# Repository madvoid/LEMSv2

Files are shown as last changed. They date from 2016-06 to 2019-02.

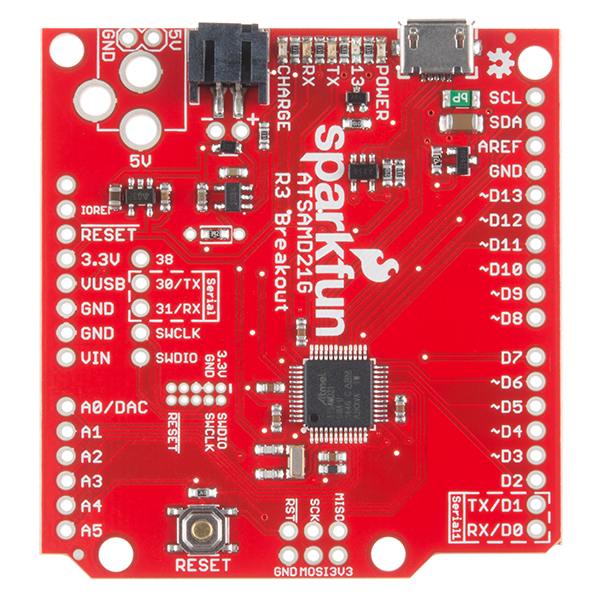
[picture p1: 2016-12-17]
Hardware Information/PCB/SAMD21 Breakout Board.jpg

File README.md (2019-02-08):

# LEMSv2
This is the repository for the second version of the LEMS Sensor Stations. Stay tuned, information will be added as it is generated. A majority of the documentation will be added to this file. Long-term future development will happen at https://github.com/UtahEFD/LEMSv2.

### General TODO

1. Check validity of filenames with more than 8 characters
2. Decagon, the manufacturer of the 5TM soil sensors, has changed their name to Meter, and the 5TM is now called the ECH20 5TM. The DS2 is now called the Atmos 22. The documentation will need to be changed and will probably be done slowly.
3. Major Change: Change the code to read parameters from a text file on the SD card. See if possible to read code from SD card.
4. Delete or separate "File List" from README? Makes it clunky, hard to keep updated. Goal is for files to self explanatory 
5. Update DS2 code to use EnviroDIY's SDI12 library instead of custom library

### PCB TODO
1. Change the parts in the eagle files for BOM lines 11, 29, 30. These parts were out of stock and were replaced by different parts during manufacturing.

### File List
* Code/
  * `Code Instructions.md` - Instructions for uploading
  * LEMSv2/
    * `LEMSv2.ino` - LEMS Arduino Code
    * `DS3231_Alarm1.h` - Header file for corresponding `.cpp` file
    * `DS3231_Alarm1.cpp` - File used to set DS3231 Alarm 1. Developed in test code then copied to this folder
    * `d5TM.h` - Header file for corresponding `.cpp` file
    * `d5TM.cpp` - Library used to interact with 5TM. Developed in test code then copied to this folder
  * Test Code/
    * ADS1115_Test/
      * `ADS1115_Test.ino` - Test code for ADS1115 ADC
    * DS3231_Test/
      * `DS3231_Test.ino` - Test code for DS3231 RTC. Test DS3231 alarm 1
      * `DS3231_Alarm1.h` - Header file for corresponding `.cpp` file
      * `DS3231_Alarm1.c` - Library used to set DS3231 Alarm 1. Developed in here then copied to main code folder
    * DS2_Test/
      * `DS2_Test.ino` - Test code for DS2 anemometer
      * `DS2.h` - Header file for corresponding `.cpp` file
      * `DS2.cpp` - Library used to interact with DS2. Developed here then copied to main code folder
      * `LICENSE` - License to be included with the `SDI12_Zero` library
      * `LICENSE-examples.md` - License to be included with the `SDI12_Zero` library
      * `SDI12_Zero.h` - Header file for corresponding `.cpp` file
      * `SDI12_Zero.cpp` - Library used by DS2 library to interact with DS2. Implements the SDI12 protocal for Arduino Zero.
    * Li200_Test/
      * `Li200_Test.ino` - Test Li200 with intermediate values in calculations printed
    * Teros21_Test/
      * `Teros21_Test.ino` - Test Teros21 and library.
    * Test_5TM/
      * `Test_5TM.ino` - Test code for 5TM Library. 5TM has been working since LEMSv1 but is now made into a library.
      * `d5TM.h` - Header file for corresponding `.cpp` file
      * `d5TM.cpp` - Library used to interact with 5TM. Developed here then copied to main code folder
  * Time_Set/
    * `Time_Set.ino` - Code used to set the time on the DS3231 real time clock
* Data Manipulation/
  * `LemsPlot.m` - View LEMSv2 data plots. Not perfectly adaptable to any file, but will work for a fully instrumented station. To work properly, requires the [Intelligent Dynamic Date Ticks](https://www.mathworks.com/matlabcentral/fileexchange/27075-intelligent-dynamic-date-ticks) file from MathWorks. Can work without it though by commenting out the lines that use it.
  * `importfile.m` - Used to import the LEMSv2 data files. Can only be used on data files from fully instrumented LEMS.
* Hardware Information/
  * `Bill of Materials.xlsx` - Complete parts list
  * `Calibration Constants.xlsx` - Calibration constants for various instruments. For now, only contains Li200 constants.
  * Data Sheets/
    * Multiple data sheets for components
  * Li200R Base/
    * Solidworks/
      * Contains Solidworks files for Li200R base
    * STL Files/
      * Contains print ready STL files for Li200R base
    * `Build Instructions.md` - Tools required for making the Li200R base
  * MLX Housing/
    * `MLX Housing Build Instructions` - Build instructions for MLX90615 housing
  * PCB/
    * `LEMSv2 Board.pdf` - PDF of PCB for easy reference
    * `LEMSv2 Schematic.pdf` - PDF of schematic for easy reference
    * `SAMD21 Breakout Board.jpg` - Reference picture for microcontroller board
  * `Pin List.xlsx` - Pin connection list for SAMD21 Dev Breakout Board
  * `Possible Parts.txt` - Potential parts/Manufacturers to add/use in the future
  * Transimpedance Amplifier/
    * `Transimpedance_Amplifier_Calculations.ipynb` - Jupyter notebook containing transimpedance amplifier calculations
  * `Wiring Information.xlsx` - Information about wiring. What connects to what, etc. Work in progress.
* `LICENSE.TXT` - License
* PCB/
  * LEMSv2 PCB/
    * `Centroid_ScreamingCircuits_smd.ulp` - Eagle ULP script to create centroid data for screaming circuits
    * Gerbers/
      * Contains gerbers for board, plus the panelized gerbers supplied by OSH Park. Also contains the centroid file for Screaming Circuits.
    * `LEMSv2.sch` - LEMSv2 shield schematic
    * `LEMSv2.brd` - LEMSv2 shield layout
    * `OSH_DesignRules.dru` - Eagle design rules for OSH Park
    * `OSHPark_2layer_Eagle7.2.cam` - Modified cam job for OSH Park
  * LEMSv2 PCB Library/
    * `LEMSv2.lbr` - Parts used in the LEMSv2 shield
* `Possible Problems.md` - List of potential hardware problems in the LEMS. Prefer to not have duplicate entries, i.e. one line per problem.
* `README.md` - If you read this line you're actually reading the README. Good job!

### Dependencies
Only 3rd party software dependencies are included in this list. Libraries built into the Arduino software or created for the LEMSv2 software isn't included. You will need the most recent version of the [Arduino IDE](https://www.arduino.cc/en/Main/Software) installed.

* [Adafruit RTC Library](https://github.com/adafruit/RTClib)
* [Adafruit SHT31 Library](https://github.com/adafruit/Adafruit_SHT31)
* [Adafruit Sensor Library](https://github.com/adafruit/Adafruit_Sensor)
* [Adafruit BMP280 Library](https://github.com/adafruit/Adafruit_BMP280_Library)
* [Adafruit MLX90614 Library](https://github.com/adafruit/Adafruit-MLX90614-Library)
* [EnviroDIY SDI-12 Library](https://github.com/EnviroDIY/Arduino-SDI-12) 
* [Soligen2010's fork of the Adafruit ADS1x15 Library](https://github.com/soligen2010/Adafruit_ADS1X15). The default Adafruit ADS1x15 library **doesn't** work.
* In addition, the Sparkfun SAMD21 [board definition](https://raw.githubusercontent.com/sparkfun/Arduino_Boards/master/IDE_Board_Manager/package_sparkfun_index.json
  ) needs to be installed into the Arduino IDE. See [here](https://learn.sparkfun.com/tutorials/samd21-minidev-breakout-hookup-guide/setting-up-arduino) for more info.

### Miscellaneous Notes

- ADS1115 single ended resolution calculation information can be found [here](https://e2e.ti.com/support/data_converters/precision_data_converters/f/73/t/489070)
- ADS1115 over range input information can be found [here](https://e2e.ti.com/support/data_converters/precision_data_converters/f/73/p/398187/1407689#1407689) and [here](https://e2e.ti.com/support/data_converters/precision_data_converters/f/73/t/378122)

### Acknowledgements

* Thanks to [Sparkfun](https://www.sparkfun.com) and [Adafruit](https://www.adafruit.com) for Arduino libraries, components, tutorials, and eagle parts. Many designs and eagle components are directly used from them. Also thanks to [OSH Park](www.oshpark.com) and [Screaming Circuits](www.screamingcircuits.com) for the excellent PCBs and assembly. They were instrumental in getting LEMSv2 completed.

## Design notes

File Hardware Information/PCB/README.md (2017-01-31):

# README.md

These files are here for quick reference. For gerber files please see the ../../PCB folder.

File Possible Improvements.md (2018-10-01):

# Possible Improvements

This document outlines possible improvements or repeatable bugs that need to be fixed.

* Multiple LEMS have now failed in an unusual way. The LEMS fails, the SD card has weird, corrupted files on it, and the LEMS may or may not blink on a restart. It is either correlated with high moisture or high electromagnetic interference (lightning). It often damages that MLX90614 beyond repair, but may damage other things. The LEMS behaves erratically after this happens.
* The DS3231 chip may reset back to 1/1/2000 00:00:00 on a restart. This is probably because of a power cycle issue, and is currently being investigated.
* Add wireless transmission for remote monitoring
* The microcontroller that runs the whole thing is currently separate from the other circuitry. It would be nice to incorporate the two so we aren’t dependent on a separate manufacturer for the boards
* The real-time clock is one of the most unreliable components on the board. Improving the reliability of this through hardware or software would improve data quality.
* Adding a GPS chip for location and accurate time would be beneficial for multiple reasons. This would help keep the real-time clock calibrated
* Making the board larger and have screw terminals for every pin would increase the flexibility of the board
* Adding electronic reliability components (fuses, transient voltage suppressors, etc.) would help with overall reliability.
* Adding a thermocouple chip would increase measurement flexibility.
* The hardware around the electronics can always use improvements!

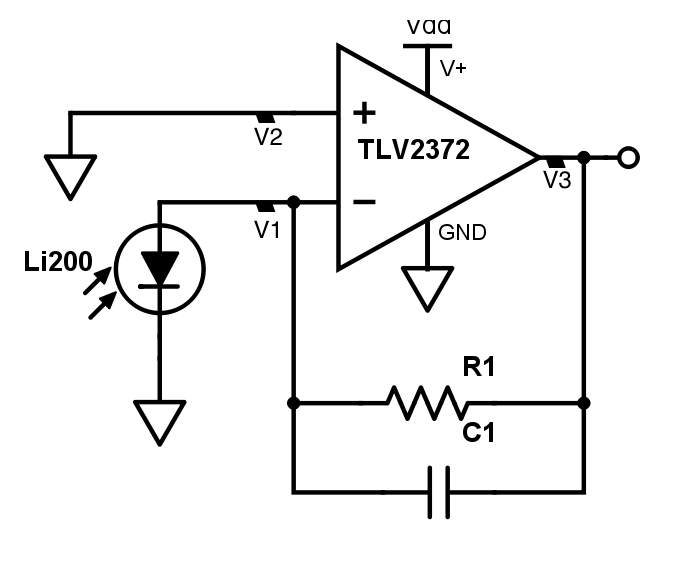
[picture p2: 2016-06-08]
Hardware Information/Transimpedance Amplifier/Li200-Transimpedance-Amplifier.png

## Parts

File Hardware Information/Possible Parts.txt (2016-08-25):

*** Possible parts to use for LEMSv2 ***
Moved from "Bill of Materials.xlsx"

Custom Enclosure:
- http://www.toollessplasticenclosures.com

Good Headers: 
- http://www.digikey.com/product-search/en/connectors-interconnects/rectangular-connectors-headers-receptacles-female-sockets/1442548?k=&pkeyword=&pv88=24&pv88=7&pv88=26&pv88=10&FV=fffc0023%2C1640001%2C1680001%2Cfff40016%2Cfff802f4&mnonly=0&newproducts=0&ColumnSort=88&page=1&stock=1&quantity=0&ptm=0&fid=0&pageSize=25

Radiation Shield: 
- http://www.ambientweather.com/amwesrpatean.html#caption
- 3D print one

Fan:
http://www.mouser.com/ProductDetail/Orion-Fans/OD4010-05MB/?qs=sGAEpiMZZMt9MS9kROxCw6QJH9LIBAB%2fCEdiIeq2Xcc%3d
http://catalog.pelonistechnologies.com/item/automotive-fans-and-blowers/all-categories-micro-fans-rfa1504u-micro-fan/rfa1504u
http://www.digikey.com/en/supplier-centers/d/delta-product-groups-fans
http://www.digikey.com/product-search/en/fans-thermal-management/dc-fans/1179730?FV=38007c%2C3800fb%2C3801a9%2Cfff40012%2Cfff80052&mnonly=0&newproducts=0&ColumnSort=2&page=3&stock=1&pbfree=0&rohs=0&quantity=&ptm=0&fid=0&pageSize=25

Jumper Cables:
- http://www.digikey.com/product-search/en/cable-assemblies/flat-flex-ribbon-jumper-cables/1573391?k=&pkeyword=&pv316=2&FV=134004e%2C13400ac%2C134019b%2C13407ff%2C134098f%2C13409fe%2C1340fa6%2Cfff40018%2Cfff8020f%2C40800cf&mnonly=0&newproducts=0&ColumnSort=0&page=1&stock=1&quantity=0&ptm=0&fid=0&pageSize=25
- http://www.digikey.com/product-search/en/cable-assemblies/flat-flex-cables-ffc-fpc/1573426?k=&pkeyword=&pv31=241&pv31=239&FV=7c00ef%2C7c00f1%2C7c00f3%2C134000c%2C1340700%2C1340736%2C1640001%2Cfff40018%2Cfff80232%2C1600006&mnonly=0&newproducts=0&ColumnSort=0&page=1&stock=1&quantity=0&ptm=0&fid=0&pageSize=25

Resettable fuse:
http://www.digikey.com/product-search/en/circuit-protection/ptc-resettable-fuses/656272?k=&pkeyword=&pv683=127&FV=400006%2C403989%2Caac0065%2Caac0073%2Caac0074%2Caac007d%2Caac007f%2Caac0090%2Caac0092%2Caac0093%2Caac0094%2Caac0095%2Caac009c%2Caac00a0%2Caac00a5%2Caac00aa%2Caac00ae%2Cfff4000a%2Cfff80390%2Caa80061&mnonly=0&newproducts=0&ColumnSort=0&page=1&stock=1&quantity=0&ptm=0&fid=0&pageSize=25

PCB Assembly:
http://pcbshopper.com
http://www.7pcb.com
https://www.screamingcircuits.com
http://www.4pcb.com/Assembly-Services.html
https://macrofab.com
https://circuithub.com

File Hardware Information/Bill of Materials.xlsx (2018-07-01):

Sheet: Full Device
 |  |  | Shipping costs and taxes not included! |  | Red cells indicate values calculated from quotes |  |  |  | Quantity: | 12
Information |  |  | Ideal Cost/Unit |  | Ideal Cost/10 Units |  | Ideal Cost/25 Units |  | Actual (Paid) Cost |  | Ordering |  |  |  | Notes
Number | Part | Quantity/Prototype | Cost/Unit | Total Quantity Cost | Cost/Unit | Prototype Cost | Cost/Unit | Prototype Cost | Cost/Unit | Prototype Cost | Source | Distributor Part Number | Package | Link
 | CR1220 Battery | 1 | $0.90 | $0.90 | $0.81 | $8.12 | $0.81 | $20.30 | $0.81 | $9.74 | Digikey | P033-ND | N/A | http://www.digikey.com/product-detail/en/panasonic-bsg/CR1220/P033-ND/269740 | Possible different source? Check footprint carefully if so
 | Noco 2.5 Watt Solar Panel | 1 | $24.95 | $24.95 | $24.95 | $249.50 | $24.95 | $623.75 | $24.95 | $299.40 | Amazon | N/A | N/A | https://www.amazon.com/NOCO-Battery-BLSOLAR2-Charger-Maintainer/dp/B00B7GC50Y | Other options available, see https://no.co/products/solar. Noco UPC: 0-46221-12069-1. More expensive on Noco website. Also known as BLSOLAR2
 | Noco 12V 2A Regulator | 1 | $12.95 | $12.95 | $12.95 | $129.50 | $12.95 | $323.75 | $12.95 | $155.40 | Amazon | N/A | N/A | https://www.amazon.com/NOCO-GC027-12V-Flex-Regulator/dp/B00H36Y65O | Other options available, see https://no.co/products/solar. Noco UPC: 0-46221-13106-2. More expensive on Noco website. Also known as GC027
 | SAMD21 Dev Board | 1 | $24.95 | $24.95 | $23.70 | $237.00 | $22.46 | $561.50 | $23.70 | $284.40 | Sparkfun | DEV-13672 | N/A | https://www.sparkfun.com/products/13672
 | Arduino Stacking Headers | 1 | $1.95 | $1.95 | $1.75 | $17.55 | $1.75 | $43.88 | $1.75 | $21.06 | Digikey | 1528-1074-ND | N/A | http://www.digikey.com/product-search/en?mpart=85&vendor=1528 | Alt. Source: https://www.adafruit.com/product/85
 | Printed Circuit Board (PCB) | 1 | $16.34 | $16.34 | $16.34 | $163.37 | $16.34 | $408.42 | $27.62 | $331.50 | Osh Park | N/A | N/A | http://www.oshpark.com | 3.38"x2.90" standard. 7.46"x6.51" panelized. 4x/panel. Osh Park prices $5/in^2 for 3. Actual cost has super swift service added. Medium run not considered
 | PCB Assembly | 1 | $70.73 | $70.73 | $70.73 | $707.33 | $70.73 | $1768.31 | $70.73 | $848.79 | Screaming Circuits | N/A | N/A | http://www.screamingcircuits.com | Ideal costs are hard to calculate without quote. Student discount included
 | PCB Turnkey Parts | 1 | $58.59 | $58.59 | $58.59 | $585.94 | $58.59 | $1464.85 | $58.59 | $703.13 | Screaming Circuits | N/A | N/A | http://www.screamingcircuits.com | Ideal costs are hard to calculate without quote. See Shield Parts sheet for part breakdown without "Turnkey Tax"
 | 12V 5.5Ah Sealed Lead Acid Battery | 1 | $8.39 | $8.39 | $8.39 | $83.90 | $8.39 | $209.75 | $32.00 | $384.00 | BatterySharks | N/A | N/A | https://www.batterysharks.com/12-Volt-5-5-Amp-Sealed-Lead-Acid-Battery-p/12v-5.5ah_ups12-5.5.htm | BatterySharks is US source. The $30 ones were bought in europe, explaining the price. F2 terminals are typically used
 | Seahorse SE-120 Waterproof Case | 1 | $11.83 | $11.83 | $11.83 | $118.30 | $11.83 | $295.75 | $11.83 | $141.96 | Fuerte Cases | SE-120 | N/A | http://www.seahorsecases.com/Seahorse-SE120-Small-Waterproof-Protective-Equipment-Storage-Shipping-Case.html | Available from other sources
 | Radiation Shield | 1 | $39.99 | $39.99 | $39.99 | $399.90 | $39.99 | $999.75 | $39.99 | $479.88 | Ambient Weather | SRS100LX | N/A | http://www.ambientweather.com/amwesrpatean.html | Sometimes available from other sources
 | SHT31 Temp/RH Sensor | 1 | $13.95 | $13.95 | $12.56 | $125.60 | $12.56 | $314.00 | $12.56 | $150.72 | Adafruit | 2857 | N/A | https://www.adafruit.com/products/2857
 | MLX90614 IR Sensor | 1 | $14.95 | $14.95 | $13.46 | $134.60 | $13.46 | $336.50 | $13.46 | $161.52 | Acrobotic | MLX90614 | N/A | https://acrobotic.com/brk-00018 | Can maybe be found on eBay
 | Decagon 5TM Soil Sensor | 2 | $186.00 | $372.00 | $167.00 | $3340.00 | $167.00 | $8350.00 | $334.00 | $4008.00 | Decagon | 5TM | N/A | https://www.decagon.com/en/ | Need quote to order
 | Davis Anemometer | 1 | $106.99 | $106.99 | $106.99 | $1069.90 | $106.99 | $2674.75 | $106.99 | $1283.88 | Hodges Marine | DAV6410 | N/A | http://www.hodgesmarine.com/Davis-Anemometer-F-Vantage-Pro2-153-Vantage-p/dav6410.htm
 | LiCor Li200 Pyranometer | 1 | $270.00 | $270.00 | $259.20 | $2592.00 | $259.20 | $6480.00 | $259.20 | $3110.40 | LiCor | Li-200R | N/A | https://www.licor.com | Can order online or with quote. Unsure whether online gets you quantity discount
 | Wide Range 1/8" Blind Rivet | 3 | $0.08 | $0.25 | $0.08 | $2.46 | $0.08 | $6.14 | $0.25 | $2.95 | McMaster | 97530A030 | N/A | https://www.mcmaster.com/#97530a030/=14t3x41 | Comes in box of 100
 | 1/8" Thick Aluminum Strip | 1 | $0.32 | $0.32 | $0.32 | $3.17 | $0.32 | $7.93 | $0.32 | $3.80 | McMaster | 2474T11 | 6' Long, 1" Wide | https://www.mcmaster.com/#2474t11/=14txki1 | Can get in orders of different lengths
 | Dessicant | 1 | $1.10 | $1.10 | $1.10 | $10.96 | $1.10 | $27.40 | $1.10 | $13.15 | McMaster | 3492T15 | N/A | https://www.mcmaster.com/#3492t15/=14r8wyx | Comes in box of 10
 | Silicone Sealing Washer | 2 | $0.15 | $0.29 | $0.15 | $2.94 | $0.15 | $7.36 | $0.29 | $3.53 | McMaster | 99604A103 | N/A | https://www.mcmaster.com/#99604a103/=14t3xma | Comes in box of 50
 | LiCor Leveling Base | 1 | $22.84 | $22.84 | $22.84 | $228.39 | $22.84 | $570.97 | $22.84 | $274.06 | - | - | - | - | See LiCor_Leveling_Base sheet for details
 | 1/4" Washer | 2 | $0.03 | $0.07 | $0.03 | $0.66 | $0.03 | $1.65 | $0.03 | $0.40 | McMaster | 90107A029 | N/A | https://www.mcmaster.com/#90107a029/=1dc0vgi | Goes around silicon washer to add thickness for rivet to clamp onto. Comes in packs of 100
 | 1&5/16" to 2&1/4" Hose Clamp | 2 | $0.70 | $1.40 | $0.70 | $13.98 | $0.70 | $34.95 | $0.70 | $8.39 | McMaster | 5415K18 | N/A | https://www.mcmaster.com/#5415k18/=178w5hq | Comes in packs of 10
 | SD Card | 1 | $4.55 | $4.55 | $4.55 | $45.50 | $4.55 | $113.75 | $4.55 | $54.60 | Newegg | 9SIA12K0X38348 | N/A | http://www.newegg.com/Product/Product.aspx?item=N82E16820134717 | Can be substituted with other parts
 | MLX90614 Housing | 1 | $6.68 | $6.68 | $6.68 | $66.84 | $6.68 | $167.11 | $6.68 | $80.21 | - | - | - | - | See MLX90614_Housing sheet for details
 |  |  |  | $0.00 |  | $0.00 |  | $0.00 |  | $0.00
 |  |  |  | $0.00 |  | $0.00 |  | $0.00 |  | $0.00
 |  |  | Total Prototype Cost: | $1086.95 | Total Prototype Cost: | $10337.41 | Total Prototype Cost: | $25812.52 | Total Prototype Cost: | $12814.88
 |  |  | Prototype Cost/Unit: | $1086.95 | Prototype Cost/Unit: | $1033.74 | Prototype Cost/Unit: | $1032.50 | Prototype Cost/Unit: | $1067.91

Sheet: Shield Parts
TH = Through Hole |  | SMT = Surface Mount | Shipping costs not included! | Octopart has alt. distributors
Information |  |  |  |  |  | Price/Unit |  | Price/10 Units |  | Price/25 Units |  | Ordering |  |  |  | Notes
Place | Reference Designator | Manufacturer | Manufacturer Part Number | Part Description | Quantity/Board | Cost/Part | Total Quantity Cost | Cost/Part | Total Quantity Cost | Cost/Part | Total Quantity Cost | Source | Distributor Part Number | Package | Distributor Link
Yes | J7, J15-J26 | On Shore Technology Inc. | OSTTE020104 | 2-Pin 3.5mm Screw Terminal | 13 | $0.3800 | $4.94 | $0.3640 | $47.32 | $0.3120 | $101.40 | Digikey | ED2740-ND | 3.5mm Spacing TH | http://www.digikey.com/product-detail/en/on-shore-technology-inc/OSTTE020104/ED2740-ND/2351816
Yes | J27-J30 | On Shore Technology Inc. | OSTTE040104 | 3-Pin 3.5mm Screw Terminal | 4 | $0.6700 | $2.68 | $0.6240 | $24.96 | $0.5616 | $56.16 | Digikey | ED2742-ND | 3.5mm Spacing TH | http://www.digikey.com/product-detail/en/on-shore-technology-inc/OSTTE040104/ED2742-ND/2351818
Yes | PS1 | Traco Power | TSR 1-2450 | DC/DC 5V Regulator | 1 | $6.2000 | $6.20 | $5.7000 | $57.00 | $5.4300 | $135.75 | Mouser | 495-TSR-1-2450 | SIP-3 | http://www.mouser.com/ProductDetail/TRACO-Power/TSR-1-2450/?qs=ckJk83FOD0XFKqda0Mzkgw%3D%3D
No | C1 | Panasonic Electronics | ECA-1HM220 | 22uF 50V Capacitor | 1 | $0.2200 | $0.22 | $0.1530 | $1.53 | $0.1124 | $2.81 | Digikey | P5179-ND | 5mm Diam. Radial TH | http://www.digikey.com/product-detail/en/ECA-1HM220/P5179-ND/245038?curr=usd&WT.z_cid=ref_octopart_dkc_buynow&site=us
Yes | U1 | TE Connectivity | 2041021-3 | SD Card Holder | 1 | $1.7400 | $1.74 | $1.7400 | $17.40 | $1.4900 | $37.25 | Newark | 35R2925 | N/A | http://www.newark.com/te-connectivity/2041021-3/memory-card-connector-sd-9-position/dp/35R2925?CMP=AFC-QO1721829242?gross_price=
Yes | U2 | Maxim Integrated | DS3231SN#T&R | DS3231 Real Time Clock | 1 | $9.9700 | $9.97 | $9.4100 | $94.10 | $7.5276 | $188.19 | Digikey | DS3231SN#T&RCT-ND | SOIC-16 | http://www.digikey.com/product-detail/en/DS3231SN%2523T%26R/DS3231SN%2523T%26RCT-ND/3894827?curr=usd&WT.z_cid=ref_octopart_dkc_buynow&site=us
Yes | R1-R5, R7, R9, R11, R13, R19-R21 | Yageo | RC0805FR-0710KL | 10k 1% 1/8W Resistor | 12 | $0.1000 | $1.20 | $0.0210 | $2.52 | $0.0152 | $4.56 | Digikey | 311-10.0KCRCT-ND | 0805 (Imperial) | http://www.digikey.com/product-detail/en/RC0805FR-0710KL/311-10.0KCRCT-ND/730482?curr=usd&WT.z_cid=ref_octopart_dkc_buynow&site=us
Yes | C2, C4, C7 | Taiyo Yuden | UMK212B7105KG-T | 1uF 50V Ceramic Capacitor | 3 | $0.2100 | $0.63 | $0.1410 | $4.23 | $0.1410 | $10.57 | Digikey | 587-2910-1-ND | 0805 (Imperial) | https://www.digikey.com/product-detail/en/taiyo-yuden/UMK212B7105KG-T/587-2910-1-ND/2649030
Yes | BT1 | Keystone Electronics | 3000 | 12mm Battery Holder | 1 | $0.5800 | $0.58 | $0.5450 | $5.45 | $0.5450 | $13.63 | Digikey | 36-3000-ND | SMT | http://www.digikey.com/product-detail/en/3000/36-3000-ND/227440?curr=usd&WT.z_cid=ref_octopart_dkc_buynow&site=us
Yes | LED1 | Lite-On Inc. | LTST-C190GKT | Green LED | 1 | $0.2700 | $0.27 | $0.1960 | $1.96 | $0.1448 | $3.62 | Digikey | 160-1183-1-ND | 0603 (Imperial) | http://www.digikey.com/product-detail/en/LTST-C190GKT/160-1183-1-ND/269255?curr=usd&WT.z_cid=ref_octopart_dkc_buynow&site=us
Yes | LED2 | Lite-On Inc. | LTST-C190KRKT | Red LED | 1 | $0.2700 | $0.27 | $0.1960 | $1.96 | $0.1448 | $3.62 | Digikey | 160-1436-1-ND | 0603 (Imperial) | http://www.digikey.com/product-detail/en/LTST-C190KRKT/160-1436-1-ND/386816?curr=usd&WT.z_cid=ref_octopart_dkc_buynow&site=us
Yes | R6, R8, R10, R17, R18 | Yageo | RC0805FR-074K3L | 4.3k 1% 1/8W Resistor | 5 | $0.1000 | $0.50 | $0.0210 | $1.05 | $0.0152 | $1.90 | Digikey | 311-4.30KCRCT-ND | 0805 (Imperial) | http://www.digikey.com/product-detail/en/RC0805FR-074K3L/311-4.30KCRCT-ND/730862?curr=usd&WT.z_cid=ref_octopart_dkc_buynow&site=us
Yes | R15, R16 | Yageo | RC0805FR-07130RL | 130 Ohm 1% 1/8W Resistor | 2 | $0.1000 | $0.20 | $0.0210 | $0.42 | $0.0152 | $0.76 | Digikey | 311-130CRCT-ND | 0805 (Imperial) | http://www.digikey.com/product-detail/en/RC0805FR-07130RL/311-130CRCT-ND/730536?curr=usd&WT.z_cid=ref_octopart_dkc_buynow&site=us
Yes | Q3, Q4, Q6, Q8, Q9 | Micro Commercial Co | MMBT3904-TP | NPN Transistor | 5 | $0.1000 | $0.50 | $0.0860 | $4.30 | $0.0784 | $9.80 | Digikey | MMBT3904TPMSCT-ND | SOT-23 | https://www.digikey.com/products/en?keywords=MMBT3904TPMSCT-ND
Yes | FB1 | TDK Corp. | MMZ2012Y152BT000 | 1.5kOhm Imp. 400 mOhm Ferrite Bead | 1 | $0.1100 | $0.11 | $0.0880 | $0.88 | $0.0880 | $2.20 | Digikey | 445-1560-1-ND | 0805 (Imperial) | http://www.digikey.com/product-detail/en/MMZ2012Y152BT000/445-1560-1-ND/571890?curr=usd&WT.z_cid=ref_octopart_dkc_buynow&site=us
Yes | C8 | Murata | GRM2165C1H102JA01D | 1000pF 50V Ceramic Capacitor | 1 | $0.1200 | $0.12 | $0.0880 | $0.88 | $0.0880 | $2.20 | Digikey | 490-1622-1-ND | 0805 (Imperial) | https://www.digikey.com/products/en?keywords=490-1622-1-ND
Yes | U5 | Texas Instruments | ADS1115IDGSR | 16-bit 4-Channel ADC | 1 | $5.6500 | $5.65 | $5.0720 | $50.72 | $5.0720 | $126.80 | Digikey | 296-38849-1-ND | 10-MSOP | http://www.digikey.com/product-detail/en/ADS1115IDGSR/296-38849-1-ND/5142969?curr=usd&WT.z_cid=ref_octopart_dkc_buynow&site=us
Yes | S1 | E-Switch | EG1218 | SPDT Switch | 1 | $0.5600 | $0.56 | $0.5420 | $5.42 | $0.5310 | $13.28 | Mouser | 612-EG1218 | 2.5mm TH | http://www.mouser.com/ProductDetail/E-Switch/EG1218/?qs=sGAEpiMZZMtHXLepoqNyVZDOWY7elTCOE4MJ3sXRkSs%3d
Yes | J1 | Sullins Connector | PPPC032LFBN-RC | 2x3 TH Female Header | 1 | $0.8200 | $0.82 | $0.6400 | $6.40 | $0.5968 | $14.92 | Digikey | S7106-ND | 0.1" TH | http://www.digikey.com/product-detail/en/sullins-connector-solutions/PPPC032LFBN-RC/S7106-ND/810243 | TH is used instead of SMT because the SMT parts are considered through hole by assembly house if not covered in tape
Yes | J2 | Sullins Connector | PPPC051LFBN-RC | 1x5 TH Female Header | 1 | $0.6500 | $0.65 | $0.5020 | $5.02 | $0.4676 | $11.69 | Digikey | S7038-ND | 0.1" TH | http://www.digikey.com/product-detail/en/sullins-connector-solutions/PPPC051LFBN-RC/S7038-ND/810177 | TH is used instead of SMT because the SMT parts are considered through hole by assembly house if not covered in tape
Yes | J3 | Sullins Connector | PPPC061LFBN-RC | 1x6 TH Female Header | 1 | $0.7000 | $0.70 | $0.5460 | $5.46 | $0.5088 | $12.72 | Digikey | S7039-ND | 0.1" TH | http://www.digikey.com/product-detail/en/sullins-connector-solutions/PPPC061LFBN-RC/S7039-ND/810178 | TH is used instead of SMT because the SMT parts are considered through hole by assembly house if not covered in tape
Yes | J4, J5 | Sullins Connector | PPPC081LFBN-RC | 1x8 TH Female Header | 2 | $0.8900 | $1.78 | $0.6900 | $13.80 | $0.6436 | $32.18 | Digikey | S7041-ND | 0.1" TH | http://www.digikey.com/product-detail/en/sullins-connector-solutions/PPPC081LFBN-RC/S7041-ND/810180 | TH is used instead of SMT because the SMT parts are considered through hole by assembly house if not covered in tape
Yes | J6 | Sullins Connector | PPPC101LFBN-RC | 1x10 TH Female Header | 1 | $0.8400 | $0.84 | $0.6990 | $6.99 | $0.6476 | $16.19 | Digikey | S7043-ND | 0.1" TH | http://www.digikey.com/product-detail/en/sullins-connector-solutions/PPPC101LFBN-RC/S7043-ND/810182 | TH is used instead of SMT because the SMT parts are considered through hole by assembly house if not covered in tape
No | J14 |  |  | 1x1 TH Female Header | 1 |  | $0.00 |  | $0.00 |  | $0.00 |  |  | 0.1" TH |  | Future Expansion Connector
No | J13 |  |  | 1x3 TH Female Header | 1 |  | $0.00 |  | $0.00 |  | $0.00 |  |  | 0.1" TH |  | Future Expansion Connector
Yes | Q1, Q2, Q5, Q7, Q10 | ON Semiconductor | BSS138 | N-Channel MOSFET | 5 | $0.2700 | $1.35 | $0.1780 | $8.90 | $0.1780 | $22.25 | Mouser | 512-BSS138 | SOT-23 | https://www.mouser.com/ProductDetail/ON-Semiconductor-Fairchild/BSS138?qs=sGAEpiMZZMshyDBzk1/Wi1qxDdW/XBi2IwQV99jpxW8=
Yes | C3, C5, C6 | Avx Corp. | 08055F104K4T2A | 0.1uF 50V Ceramic Capacitor | 3 | $0.3800 | $1.14 | $0.2660 | $7.98 | $0.2660 | $19.95 | Digikey | 478-3614-1-ND | 0805 (Imperial) | https://www.digikey.com/products/en?keywords=478-3614-1-ND
Yes | U3 | Texas Instruments | TLV2372IDR | 2-Channel Rail-To-Rail Op-Amp | 1 | $1.6100 | $1.61 | $1.3700 | $13.70 | $1.3700 | $34.25 | Mouser | 595-TLV2372IDR | SOIC-8 | http://www.mouser.com/ProductDetail/Texas-Instruments/TLV2372IDR/
No | R14 |  |  | Gain Resistor | 1 |  | $0.00 |  | $0.00 |  | $0.00 |  |  |  |  | Not added yet
Yes | U4 | Bosch Sensortec | BMP280 | Digital Barometer | 1 | $2.2800 | $2.28 | $2.0800 | $20.80 | $1.9200 | $48.00 | Mouser | 262-BMP280 | LGA-8 | http://www.mouser.com/ProductDetail/Bosch-Sensortec/BMP280/?qs=QhAb4EtQfbUP9Z%252bCHM3Wyg%3D%3D
Yes | DS1, DS2 | Comchip Technology | CDBA240L-HF | Schottky Diode | 2 | $0.4000 | $0.80 | $0.3100 | $6.20 | $0.2612 | $13.06 | Digikey | 641-1697-1-ND | DO-214AC | http://www.digikey.com/product-detail/en/comchip-technology/CDBA240L-HF/641-1697-1-ND/5226080
Yes | R23, R24 | Yageo | RC0805FR-0775KL | 75k 1% 1/8W Resistor | 2 | $0.1000 | $0.20 | $0.0210 | $0.42 | $0.0152 | $0.76 | Digikey | 311-75.0KCRCT-ND | 0805 (Imperial) | http://www.digikey.com/product-detail/en/RC0805FR-0775KL/311-75.0KCRCT-ND/731080?curr=usd&WT.z_cid=ref_octopart_dkc_buynow&site=us
Yes | R12 | Vishay Dale | CRCW080556K0FKEA | 56k 1% 1/8W Resistor | 1 | $0.1000 | $0.10 | $0.0400 | $0.40 | $0.0288 | $0.72 | Digikey | 541-56.0KCCT-ND | 0805 (Imperial) | http://www.digikey.com/product-detail/en/CRCW080556K0FKEA/541-56.0KCCT-ND/1180982?curr=usd&WT.z_cid=ref_octopart_dkc_buynow&site=us
Yes | R22 | Yageo | RC0805FR-0716KL | 16k 1% 1/8W Resistor | 1 | $0.1000 | $0.10 | $0.0210 | $0.21 | $0.0152 | $0.38 | Digikey | 311-16.0KCRCT-ND | 0805 (Imperial) | http://www.digikey.com/product-detail/en/RC0805FR-0716KL/311-16.0KCRCT-ND/730567?curr=usd&WT.z_cid=ref_octopart_dkc_buynow&site=us
 |  |  |  | Total Placements: | 80 | Total Cost | $48.71 | Total Cost | $418.38 | Total Cost | $941.56
 |  |  |  | Through Hole Placements: | 25 | Cost/Unit | $48.71 | Cost/Unit | $41.84 | Cost/Unit | $37.66

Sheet: LiCor_Leveling_Base
 |  |  | Shipping costs and taxes not included! |  |  |  |  |  | Quantity: | 12
Information |  |  | Ideal Cost/Unit |  | Ideal Cost/10 Units |  | Ideal Cost/25 Units |  | Actual (Paid) Cost |  | Ordering |  |  |  | Notes
Number | Part | Quantity/Prototype | Cost/Unit | Total Quantity Cost | Cost/Unit | Prototype Cost | Cost/Unit | Prototype Cost | Cost/Unit | Prototype Cost | Source | Distributor Part Number | Package | Link
 | 2" 10-32 Threaded Rod | 3 | $0.22 | $0.67 | $0.22 | $6.67 | $0.22 | $16.68 | $0.67 | $8.01 | McMaster | 95475A509 | N/A | https://www.mcmaster.com/#95475a509/=14txpr7 | Comes in box of 50
 | 10-32 Wing Nut | 3 | $0.09 | $0.27 | $0.09 | $2.66 | $0.09 | $6.64 | $0.27 | $3.19 | McMaster | 90866A111 | N/A | https://www.mcmaster.com/#90866a111/=14txqey | Comes in box of 100
 | Compression Spring | 3 | $0.86 | $2.59 | $0.86 | $25.88 | $0.86 | $64.69 | $2.59 | $31.05 | McMaster | 9657K276 | N/A | https://www.mcmaster.com/#9657k276/=14txsar | Comes in box of 12
 | 10-32 Right Hand Helicoil | 4 | $0.61 | $2.46 | $0.61 | $24.60 | $0.61 | $61.50 | $2.46 | $29.52 | McMaster | 91732A725 | N/A | https://www.mcmaster.com/#91732a725/=14ty2ad | Comes in box of 10
 | 10-32 Thread Set Screw | 4 | $0.12 | $0.48 | $0.12 | $4.83 | $0.12 | $12.08 | $0.48 | $5.80 | McMaster | 92311A832 | N/A | https://www.mcmaster.com/#92311A832 | Comes in box of 50
 | Bubble Level | 1 | $3.14 | $3.14 | $3.14 | $31.40 | $3.14 | $78.50 | $3.14 | $37.68 | McMaster | 2147A61 | N/A | https://www.mcmaster.com/#2147a61/=14ty9lt
 | 4" Long, Thick Wall PVC Unthreaded 3/4 Pipe Size | 1 | $0.32 | $0.32 | $0.32 | $3.17 | $0.32 | $7.92 | $0.32 | $3.80 | McMaster | 48855K22 | N/A | https://www.mcmaster.com/#48855K22 | Comes in lengths of 5'. Other lengths available
 | 3D Printed Plates | 1 | $12.92 | $12.92 | $12.92 | $129.18 | $12.92 | $322.96 | $12.92 | $155.02 | UofU ME Dept. | N/A | N/A |  | Pricing is for UofU Mechanical Engineering Dept. printer
 |  |  |  | $0.00 |  | $0.00 |  | $0.00 |  | $0.00
 |  |  |  | $0.00 |  | $0.00 |  | $0.00 |  | $0.00
 |  |  |  | $0.00 |  | $0.00 |  | $0.00 |  | $0.00
 |  |  |  | $0.00 |  | $0.00 |  | $0.00 |  | $0.00
 |  |  |  | $0.00 |  | $0.00 |  | $0.00 |  | $0.00
 |  |  |  | $0.00 |  | $0.00 |  | $0.00 |  | $0.00
 |  |  |  | $0.00 |  | $0.00 |  | $0.00 |  | $0.00
 |  |  |  | $0.00 |  | $0.00 |  | $0.00 |  | $0.00
 |  |  |  | $0.00 |  | $0.00 |  | $0.00 |  | $0.00
 |  |  |  | $0.00 |  | $0.00 |  | $0.00 |  | $0.00
 |  |  |  | $0.00 |  | $0.00 |  | $0.00 |  | $0.00
 |  |  |  | $0.00 |  | $0.00 |  | $0.00 |  | $0.00
 |  |  |  | $0.00 |  | $0.00 |  | $0.00 |  | $0.00
 |  |  |  | $0.00 |  | $0.00 |  | $0.00 |  | $0.00
 |  |  |  | $0.00 |  | $0.00 |  | $0.00 |  | $0.00
 |  |  |  | $0.00 |  | $0.00 |  | $0.00 |  | $0.00
 |  |  |  | $0.00 |  | $0.00 |  | $0.00 |  | $0.00
 |  |  |  | $0.00 |  | $0.00 |  | $0.00 |  | $0.00
 |  |  |  | $0.00 |  | $0.00 |  | $0.00 |  | $0.00
 |  |  | Total Prototype Cost: | $22.84 | Total Prototype Cost: | $228.39 | Total Prototype Cost: | $570.97 | Total Prototype Cost: | $274.06
 |  |  | Prototype Cost/Unit: | $22.84 | Prototype Cost/Unit: | $22.84 | Prototype Cost/Unit: | $22.84 | Prototype Cost/Unit: | $22.84

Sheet: MLX90614_Housing
 |  |  | Shipping costs and taxes not included! |  |  |  |  |  | Quantity: | 12
Information |  |  | Ideal Cost/Unit |  | Ideal Cost/10 Units |  | Ideal Cost/25 Units |  | Actual (Paid) Cost |  | Ordering |  |  |  | Notes
Number | Part | Quantity/Prototype | Cost/Unit | Total Quantity Cost | Cost/Unit | Prototype Cost | Cost/Unit | Prototype Cost | Cost/Unit | Prototype Cost | Source | Distributor Part Number | Package | Link
 | PVC T Conduit | 1 | $2.48 | $2.48 | $2.48 | $24.80 | $2.48 | $62.00 | $2.48 | $29.76 | Lowe's | 115991 | N/A | https://www.lowes.com/pd/CARLON-1-2-in-PVC-Transition/3127629
 | PVC Elbow | 1 | $0.65 | $0.65 | $0.65 | $6.50 | $0.65 | $16.25 | $0.65 | $7.80 | Lowe's | 50916 | N/A | https://www.lowes.com/pd/CARLON-1-2-in-Schedule-40-PVC-Elbow/1091493
 | PVC 90-Degree T Fitting | 1 | $0.39 | $0.39 | $0.39 | $3.90 | $0.39 | $9.75 | $0.39 | $4.68 | Lowe's | 23873 | N/A | https://www.lowes.com/pd/LASCO-1-2-in-Dia-90-Degree-PVC-Sch-40-Tee/1067651
 | Faucet Repair Kit | 1 | $0.99 | $0.99 | $0.99 | $9.90 | $0.99 | $24.75 | $0.99 | $11.88 | Lowe's | 502098 | N/A | https://www.lowes.com/pd/BrassCraft-Faucet-Repair-Kit/4778474 | Only need screen, not washer
 | 1/2" PVC Coupling | 1 | $0.33 | $0.33 | $0.33 | $3.30 | $0.33 | $8.25 | $0.33 | $3.96 | Lowe's | 23761 | N/A | https://www.lowes.com/pd/Genova-1-2-in-Dia-Coupling-CPVC-Fittings/1000200923
 | Rubber Flat Washer | 1 | $0.54 | $0.54 | $0.54 | $5.35 | $0.54 | $13.38 | $0.54 | $6.42 | Lowe's | 423565 | N/A | https://www.lowes.com/pd/The-Hillman-Group-2-Count-5-16-in-x-1-1-4-in-Rubber-Standard-SAE-Flat-Washers/4582595 | Comes in 2 pack
 | Zinc-Plated Standard Washer | 1 | $0.29 | $0.29 | $0.29 | $2.88 | $0.29 | $7.19 | $0.29 | $3.45 | Lowe's | 136616 | N/A | https://www.lowes.com/pd/The-Hillman-Group-4-Count-1-4-in-x-1-in-Zinc-Plated-Standard-SAE-Fender-Washers/3012355 | Comes in 4 pack
 | 1-5/16" to 2-1/4" Hose Clamp | 1 | $1.02 | $1.02 | $1.02 | $10.22 | $1.02 | $25.55 | $1.02 | $12.26 | Lowe's | 94579 | N/A | https://www.lowes.com/pd/10-Pack-1-5-16-in-to-2-1-4-in-dia-Stainless-Steel-Adjustable-Clamps/3878586 | Comes in 10 pack
 |  |  |  | $0.00 |  | $0.00 |  | $0.00 |  | $0.00
 |  |  |  | $0.00 |  | $0.00 |  | $0.00 |  | $0.00
 |  |  |  | $0.00 |  | $0.00 |  | $0.00 |  | $0.00
 |  |  |  | $0.00 |  | $0.00 |  | $0.00 |  | $0.00
 |  |  |  | $0.00 |  | $0.00 |  | $0.00 |  | $0.00
 |  |  |  | $0.00 |  | $0.00 |  | $0.00 |  | $0.00
 |  |  |  | $0.00 |  | $0.00 |  | $0.00 |  | $0.00
 |  |  |  | $0.00 |  | $0.00 |  | $0.00 |  | $0.00
 |  |  |  | $0.00 |  | $0.00 |  | $0.00 |  | $0.00
 |  |  |  | $0.00 |  | $0.00 |  | $0.00 |  | $0.00
 |  |  |  | $0.00 |  | $0.00 |  | $0.00 |  | $0.00
 |  |  |  | $0.00 |  | $0.00 |  | $0.00 |  | $0.00
 |  |  |  | $0.00 |  | $0.00 |  | $0.00 |  | $0.00
 |  |  |  | $0.00 |  | $0.00 |  | $0.00 |  | $0.00
 |  |  |  | $0.00 |  | $0.00 |  | $0.00 |  | $0.00
 |  |  |  | $0.00 |  | $0.00 |  | $0.00 |  | $0.00
 |  |  |  | $0.00 |  | $0.00 |  | $0.00 |  | $0.00
 |  |  |  | $0.00 |  | $0.00 |  | $0.00 |  | $0.00
 |  |  |  | $0.00 |  | $0.00 |  | $0.00 |  | $0.00
 |  |  | Total Prototype Cost: | $6.68 | Total Prototype Cost: | $66.84 | Total Prototype Cost: | $167.11 | Total Prototype Cost: | $80.21
 |  |  | Prototype Cost/Unit: | $6.68 | Prototype Cost/Unit: | $6.68 | Prototype Cost/Unit: | $6.68 | Prototype Cost/Unit: | $6.68
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

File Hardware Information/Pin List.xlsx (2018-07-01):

Note: 3.3V/Ground connections not shown unless necessary
Pin | Alt. Name | Connection | Screw Terminal Connection | PCB Connection Checklist
D0 | Serial1 RX | Upper 5TM Data/Upper Teros21 Data | 1 | Yes
D1 | Serial1 TX |  | 0 | N/A
D2 |  | Upper 5TM Power/Upper Teros21 Power | 1 | Yes
D3 |  |  | 0 | N/A
D4 |  | Fan Pin | 1 | Yes
D5 |  | SD Card Chip Select | 0 | Yes
D6 |  | Green LED | 0 | Yes
D7 |  | Red LED | 0 | Yes
D8 |  | Davis Wind Speed | 1 | Yes
D9 |  | RTC Alarm Pin | 0 | Yes
D10 |  | Sonic Anemometer Pin (5V) | 1 | Yes
D11 |  |  | 0 | N/A
D12 |  |  | 0 | N/A
D13 |  | On-board Blue LED | 0 | N/A
AREF |  |  | 0 | N/A
SCL |  | I2C Sensors Clock | 1 | Yes
SDA |  | I2C Sensors Data | 1 | Yes
D38 |  | Lower 5TM Power/Lower Teros21 Power | 1 | Yes
D30 | Serial TX |  | 0 | N/A
D31 | Serial RX | Lower 5TM Data/Lower Teros21 Data | 1 | Yes
SWCLK |  |  | 0 | N/A
SWDIO |  |  | 0 | N/A
IOREF |  |  | 0 | N/A
RESET |  |  | 0 | N/A
VUSB |  |  | 0 | N/A
VIN |  | 5V Regulator | 0 | Yes
A0 | DAC |  | 0 | N/A
A1 |  |  | 0 | N/A
A2 |  |  | 0 | N/A
A3 |  |  | 0 | N/A
A4 |  | Davis Wind Direction | 1 | Yes
A5 |  | Battery Resistor Divider | 0 | N/A
MISO |  | SPI Component Master-In Slave-Out | 1 | Yes
SCK |  | SPI Component Clock | 1 | Yes
MOSI |  | SPI Component Master-Out Slave-In | 1 | Yes

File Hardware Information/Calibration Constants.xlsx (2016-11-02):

Constants |  |  | LEMS Serial Number | LEMS Short Number | Serial Number | Calibration Constant (A/(Wm^-2)) | Ideal Resistor (Ohm) | Ideal Max Voltage (V) | Actual Resistor (Ohm) | Actual Max Voltage (V) | Digikey Part Number | Cost | Digikey URL
Maximum Sunlight: | 1200.0000 | W/m^2 | LEMSv22016A01 | A01 | PY80043 | 9.254e-08 | 36884.95 | 4.096 | 36500 | 4.053252 | 36.5KXBK-ND | $0.10 | http://www.digikey.com/product-detail/en/yageo/MFR-25FBF52-36K5/36.5KXBK-ND/13325
Maximum Voltage: | 4.0960 | V | LEMSv22016B01 | B01 | PY80046 | 9.007e-08 | 37896.45 | 4.096 | 37400 | 4.0423416 | 37.4KXBK-ND | $0.10 | http://www.digikey.com/product-detail/en/yageo/MFR-25FBF52-37K4/37.4KXBK-ND/13327
Rail Offset: | 0.0000 | V | LEMSv22016C01 | C01 | PY80042 | 8.606e-08 | 39662.25 | 4.096 | 39200 | 4.0482624 | 39.2KXBK-ND | $0.10 | http://www.digikey.com/product-detail/en/yageo/MFR-25FBF52-39K2/39.2KXBK-ND/13331
 |  |  | LEMSv22016D01 | D01 | PY75566 | 1.0225e-07 | 33382.23 | 4.096 | 33200 | 4.07364 | 33.2KXBK-ND | $0.10 | http://www.digikey.com/product-detail/en/yageo/MFR-25FBF52-33K2/33.2KXBK-ND/13317
 |  |  | LEMSv22016E01 | E01 | PY103188 | 5.83e-08 | 58547.74 | 4.096 | 57600 | 4.029696 | 57.6KXBK-ND | $0.10 | http://www.digikey.com/product-detail/en/yageo/MFR-25FBF52-57K6/57.6KXBK-ND/13426
 |  |  | LEMSv22016F01 | F01 | PY103189 | 5.493e-08 | 62139.69 | 4.096 | 62000 | 4.086792 | S62KCACT-ND | $0.10 | http://www.digikey.com/product-detail/en/stackpole-electronics-inc/RNMF14FTC62K0/S62KCACT-ND/2617523
 |  |  | LEMSv22016G01 | G01 | PY103190 | 5.701e-08 | 59872.54 | 4.096 | 59000 | 4.036308 | 59.0KXBK-ND | $0.10 | http://www.digikey.com/product-detail/en/yageo/MFR-25FBF52-59K/59.0KXBK-ND/13428
 |  |  | LEMSv22016H01 | H01 | PY103191 | 5.689e-08 | 59998.83 | 4.096 | 59000 | 4.027812 | 59.0KXBK-ND | $0.10 | http://www.digikey.com/product-detail/en/yageo/MFR-25FBF52-59K/59.0KXBK-ND/13428
 |  |  | LEMSv22016I01 | I01 | PY103192 | 5.717e-08 | 59704.97 | 4.096 | 59000 | 4.047636 | 59.0KXBK-ND | $0.10 | http://www.digikey.com/product-detail/en/yageo/MFR-25FBF52-59K/59.0KXBK-ND/13428
 |  |  | LEMSv22016J01 | J01 | PY103193 | 5.258e-08 | 64916.95 | 4.096 | 64900 | 4.0949304 | 64.9KXBK-ND | $0.10 | http://www.digikey.com/product-detail/en/yageo/MFR-25FBF52-64K9/64.9KXBK-ND/13436
 |  |  | LEMSv22016K01 | K01 | PY103194 | 5.78e-08 | 59054.21 | 4.096 | 59000 | 4.09224 | 59.0KXBK-ND | $0.10 | http://www.digikey.com/product-detail/en/yageo/MFR-25FBF52-59K/59.0KXBK-ND/13428
 |  |  | LEMSv22016L01 | L01 | PY103195 | 5.995e-08 | 56936.34 | 4.096 | 56200 | 4.043028 | 56.2KXBK-ND | $0.10 | http://www.digikey.com/product-detail/en/yageo/MFR-25FBF52-56K2/56.2KXBK-ND/13424

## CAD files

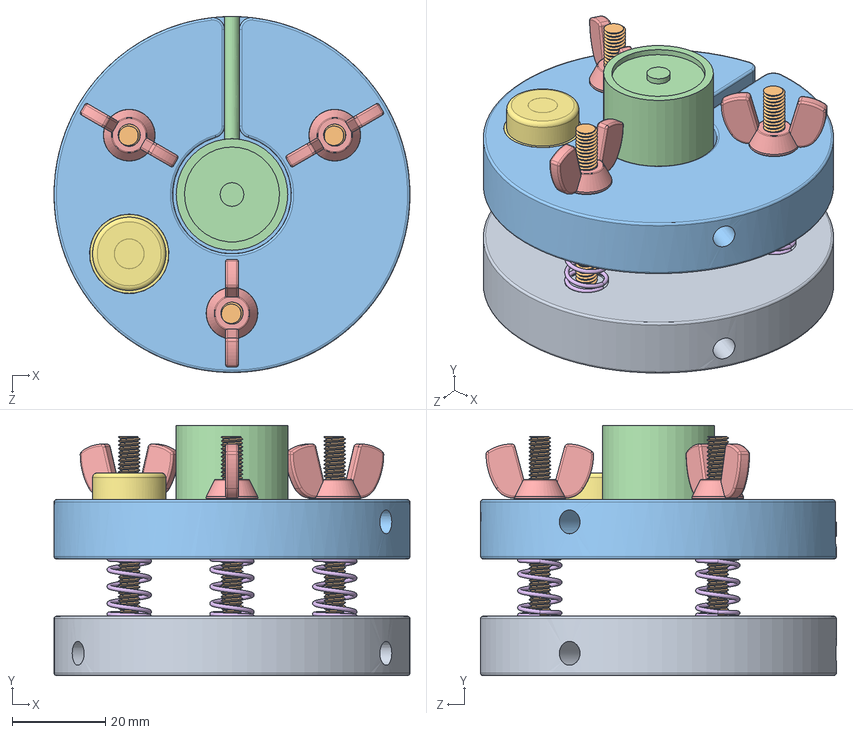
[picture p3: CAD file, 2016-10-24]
Hardware Information/Li200R Base/Solidworks/base_assy 0.375 Spring.SLDASM
76.2 x 53.5 x 76.2 mm
base_bottom
95475A509 Rod x 3
base_top
Li200
90866A111 Wingnut x 3
9657K276 Spring x 3
2147A610 Plastic Level

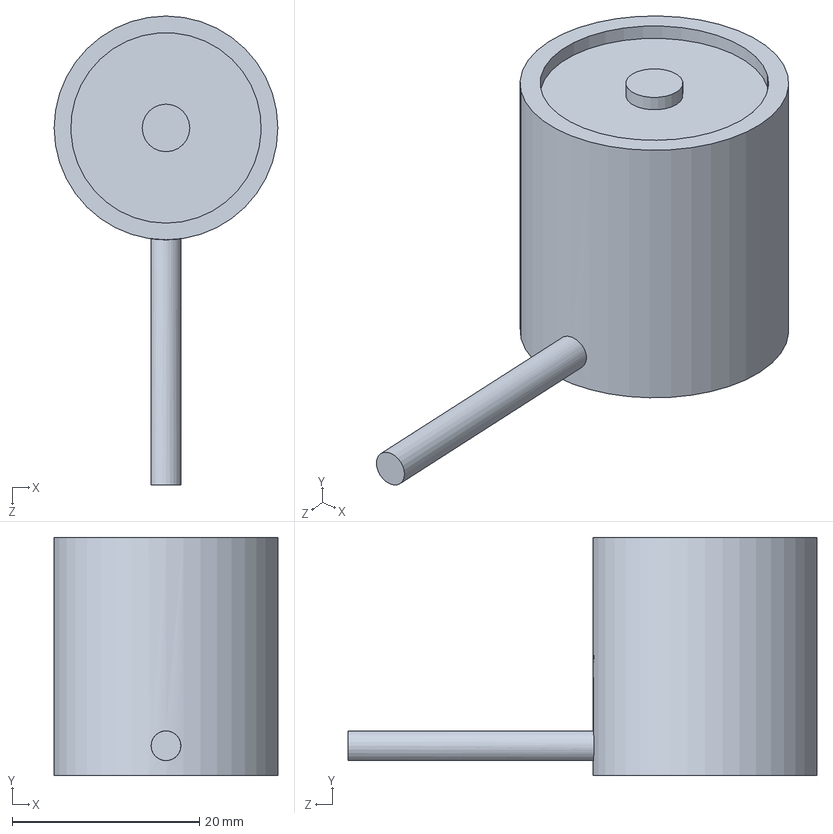
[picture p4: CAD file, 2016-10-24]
Hardware Information/Li200R Base/Solidworks/Li200.SLDPRT
23.9 x 25.4 x 50.0 mm

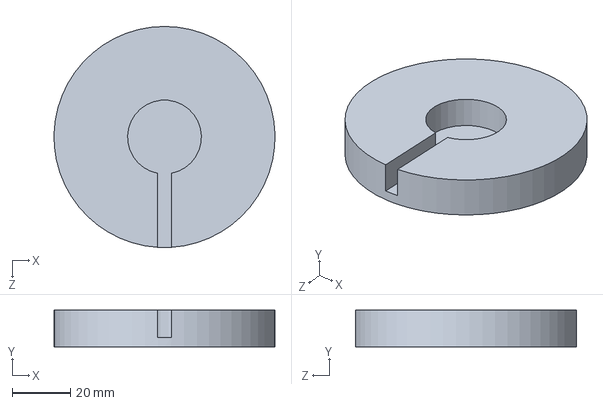
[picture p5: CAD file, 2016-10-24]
Hardware Information/Li200R Base/Solidworks/Top.SLDPRT
76.2 x 12.7 x 76.2 mm

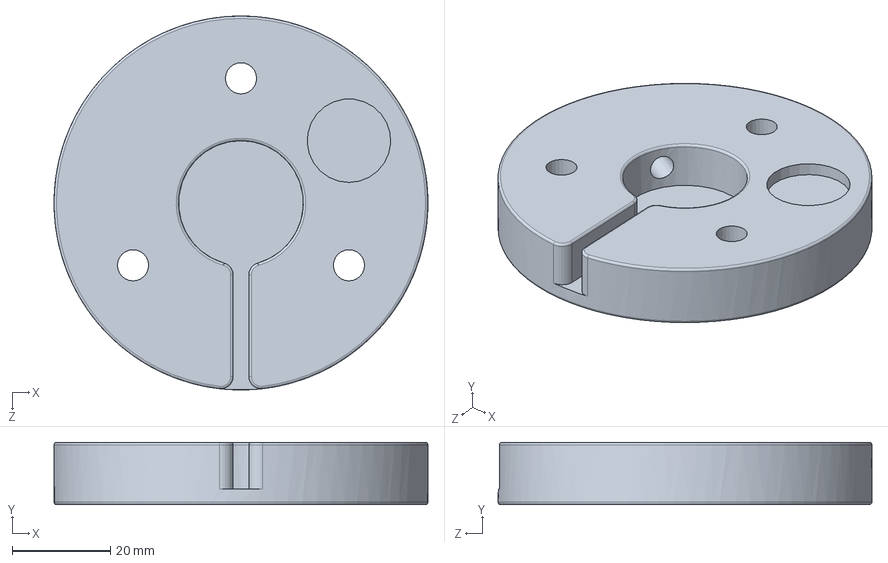
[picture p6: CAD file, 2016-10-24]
Hardware Information/Li200R Base/Solidworks/base_top.SLDPRT
76.2 x 12.7 x 76.2 mm

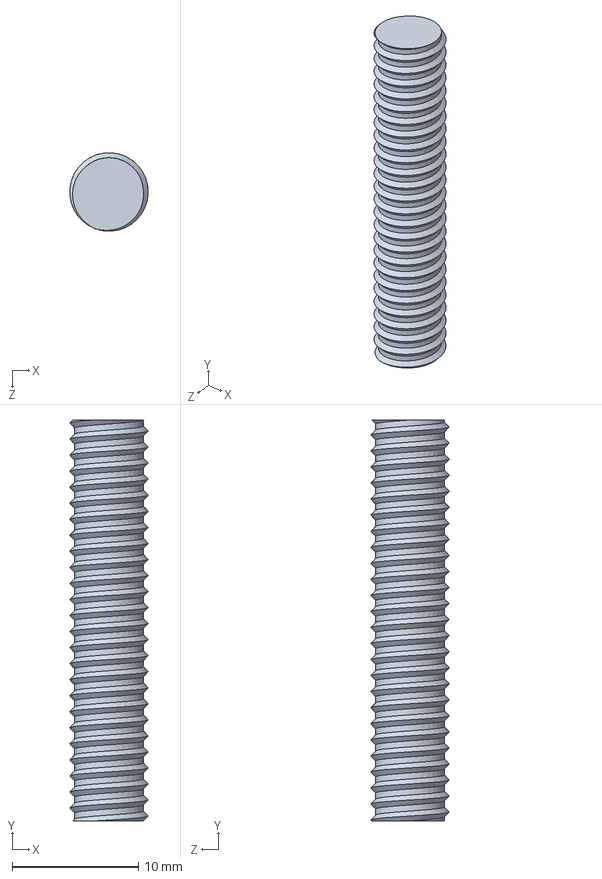
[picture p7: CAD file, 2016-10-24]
Hardware Information/Li200R Base/Solidworks/92311A544 Set Screw.SLDPRT
6.21 x 31.7 x 6.21 mm

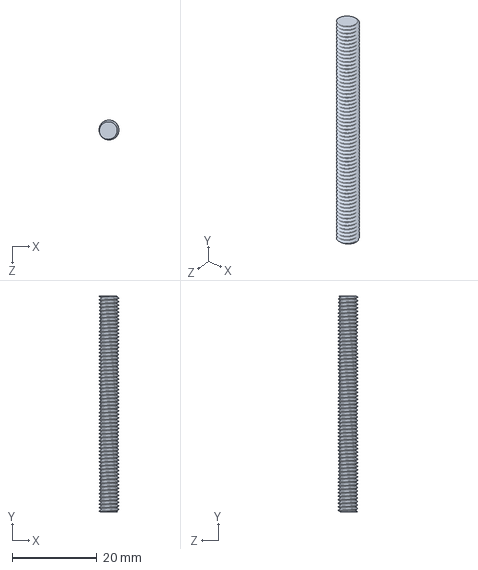
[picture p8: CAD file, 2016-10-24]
Hardware Information/Li200R Base/Solidworks/95475A509 Rod.SLDPRT
4.73 x 51.1 x 4.73 mm

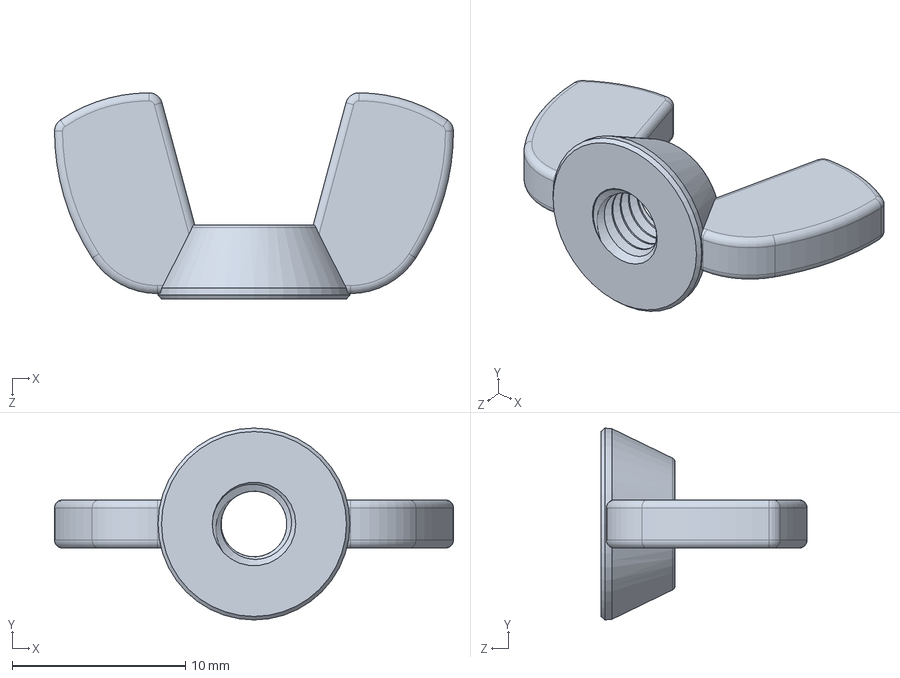
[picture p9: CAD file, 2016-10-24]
Hardware Information/Li200R Base/Solidworks/90866A111 Wingnut.SLDPRT
23.0 x 11.1 x 11.9 mm

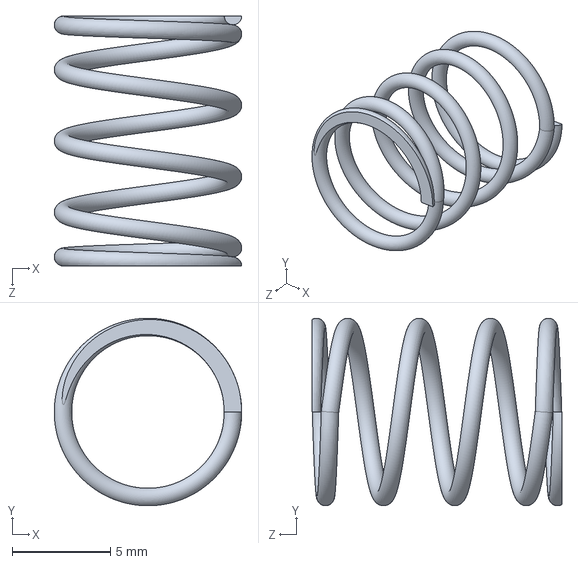
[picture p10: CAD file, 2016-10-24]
Hardware Information/Li200R Base/Solidworks/9657K276 Spring.SLDPRT
9.52 x 9.52 x 12.7 mm

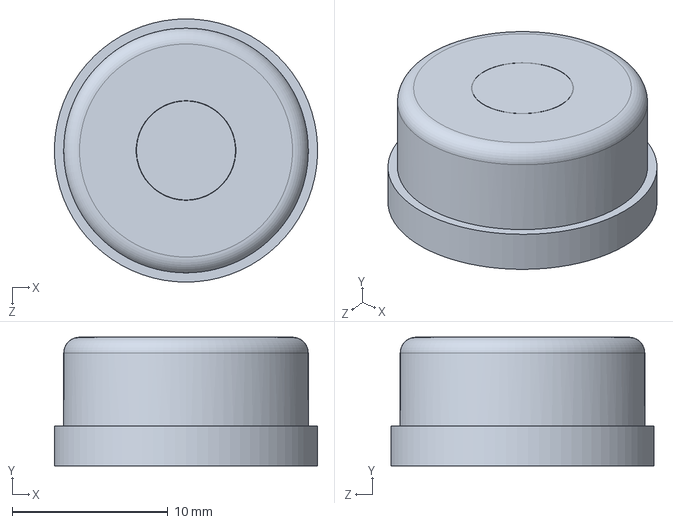
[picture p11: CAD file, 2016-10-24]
Hardware Information/Li200R Base/Solidworks/2147A610 Plastic Level.SLDPRT
16.9 x 8.26 x 16.9 mm

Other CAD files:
Hardware Information/Li200R Base/Solidworks/Bottom.SLDPRT
Hardware Information/Li200R Base/Solidworks/base_bottom.SLDPRT
Hardware Information/Li200R Base/STL Files/base_bottom.STL
Hardware Information/Li200R Base/STL Files/base_top.STL

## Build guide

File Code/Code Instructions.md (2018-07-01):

# Code Instructions

Please read through all instructions before starting!

1. Ensure all libraries and board definitions are installed (see [README.md](../README.md))

2. Obtain a LEMSv2

3. Ensure that a CR1220 coin cell battery is inserted into the RTC battery holder

4. Plug the LEMSv2 into computer via a micro-USB cable. The board should be set to `SparkFun SAMD21 Dev Breakout`. The board definition should have been installed in step 1. The COM port should be set to whatever COM port the arduino is plugged into.

5. Double press the reset button on the red SAMD21 breakout board. This puts the board in a state where it's waiting for a code to be uploaded

6. Open `Time_Set.ino` in the Arduino IDE. Compile and upload the code but do not unplug the USB cable. The RTC battery should be installed. This will set the time on the RTC to whatever time it is on the host computer. When this code is running, opening the serial monitor should display the time at regular intervals. This can be used to check the time is working.

7. While the time set code is still running, open `LEMSv2.ino` in the Arduino IDE. 

8. In lines 34 through 41 (under the "Sensor Defines" heading), set measurements to 0 or 1 depending on whether that sensor is plugged in or not. (0 for not plugged in, 1 for plugged in). The pressure sensor is soldered onto the board, so it should always be set as 1 unless there are other concerns (file size, timing, etc.)

9. On line 50 (under the "Other Defines" heading), set DEBUG to 0

10. On line 102, set the filename to a desired filename. Filenames with more than 8 characters (not counting file extension) haven't been tested. The last two characters in the filename (not counting the file extension) **need** to be base-10 numbers. It is recommended those two are left as "00".

11. On line 147, enter the LiCor Li200R calibration constant, found in `../Hardware Information/Calibration Constants.xlsx`. They should be entered in the units of (Amps/(W/m^2)). It is easiest to type the given calibration constant and divide it by 1000. For example, a calibration constant of 92.54 $\mu A$ per 1000 W/m^2^ should look like this in the code:

   ```c++
   const double liConst = 92.54E-6 / 1000;  // Licor Calibration Constant. Units of (Amps/(W/m^2))
   ```
   Of course, this doesn't matter if a Li200R isn't plugged in.

12. On line 147, enter the resistor value of the resistor soldered into R14 of the LEMSv2 PCB. This information can be found in `../Hardware Information/Calibration Constants.xlsx`. The resistor value to enter is under the *Actual Resistor* column of the spreadsheet. Enter the value in Ohms. Also, please remember that each LEMSv2 is designed to work with a specific pyranometer, which is why each LEMSv2 has a very specific resistor soldered to it. This means that using a different pyranometer on a given LEMSv2 can give less precise/accurate results.

13. Compile and upload code to the LEMSv2. Unplug soon after upload is finished so program doesn't start and file isn't made.

14. Insert an SD card into the holder

15. After wiring and installation, if a battery is plugged in, turning the switch from off to on should turn on the LEMSv2. 

16. After a short amount of time, the green light should turn on for about three seconds. If a blinking red light shows up, something is wrong. First check the SD card and make sure it works, is formatted, and is plugged in correctly.

17. After the three seconds, the green light should turn off. After that, wait until the green light blinks a few times. If the green light doesn't blink after about 20 seconds, something is wrong. Check the sensors and connections, and try power cycling the LEMSv2.

18. When everything is running properly, the green light should blink every 10 seconds. 

19. To turn off, wait until green light blinks, and turn off shortly after.

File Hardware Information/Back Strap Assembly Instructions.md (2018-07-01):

# Back Strap Instructions

This document describes how to install the aluminum bar on the back of the LEMS case (back strap).

1. The aluminum strip used should be 1/8" thick and 1" wide. Cut off a 3.5" long piece. Use a belt sander to de-burr and smooth any sharp edges. From here on, this piece will be known as the **back strap**.
2. Using a marker, put a dot 0.375" from each short edge of the 3.5" long aluminum piece. These dots are where the holes will go for the rivets.
3. Using an easily removable tape, tape the back strap to the box in the correct position. The back strap should be centered vertically and horizontally on the box.
4. Using a #30 drill (0.1285"), drill a hole on each dot. Drill through the back strap and the box at the same time. There will be a total of two holes in the back strap and box when finished.
5. Place a silicone sealing washer within a 1/4" regular washer. Repeat this process for another washer. place these two washer "assemblies" over each of the holes in the box. Place the back strap over the washers. The regular washer gives space between the back strap and the box, and the silicone washer prevents the elements from getting in.
6. Rivet the box, washers, and back strap together. The rivet head (i.e. the mandrel before installation) should be on the inside of the box.

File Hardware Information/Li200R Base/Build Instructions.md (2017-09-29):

# Build Instructions

### Tool Information

* 10-32 tap hole requires #21 [drill](http://littlemachineshop.com/reference/tapdrill.php) (.1590")
* 10-32 tap hole requires 10-32 tap
* 10-32 Helicoils require 5.1mm [drill](http://www.thorintl.com/Drill-Sizes-HeliCoils-UNC-UNF.shtml)
* 10-32 Helicoils require 10-32 STI tap
* 10-32 Helicoils require Helicoil insertion tool
* Bottom plate requires Loctite
* Plates require 3D printer
* Pipe requires saw

### Build Instructions

1. 3D print bottom and top plate. First test is with sparse fill but solid fill will work too (more expensive but better). Keep in mind that a sparse fill will absorb water better, and will also leak cleaning fluid for some time after manufacturing.
2. If the prints are completely dry, this would be a good point to paint the pieces for weather resistance
3. Tap the three holes on the face of the bottom plate with the 10-32 tap
4. Tap the three holes on the edge of the bottom plate and the one hole on the edge of the top plate with the 10-32 STI tap
5. Insert helicoils into all edge holes that have been tapped with 10-32 STI tap
6. This is another point where paint can be applied
7. Insert threaded rods with thread locker onto three holes on face of bottom plate
8. Put springs over threaded rods
9. Put top plate on top of springs through threaded rods
10. Insert bubble level into cutout on top plate
11. Thread wing nuts onto threaded rods
12. Insert section of pipe into bottom plate and tighten set screws 

### Usage Instructions

Put LiCor Li200R into top plate and tighten set screw. Zip tie pipe on bottom plate to convenient mount point. Adjust wing nuts until bubble level reads level.

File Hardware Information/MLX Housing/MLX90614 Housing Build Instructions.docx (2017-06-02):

MLX90614 Housing Build Instructions

Tool Information

- Super glue
- Soldering Iron
- Screwdriver (Probably Phillips - dependent on the screws present on T-conduit)

Assembly Instructions

1. Super glue the faucet repair kit together, and then glue the washer to the smooth rim of the coupling as shown below.

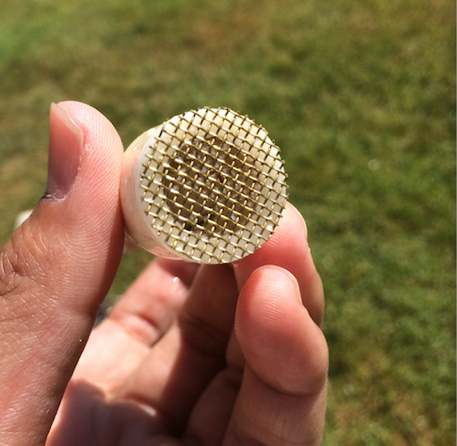
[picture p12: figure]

2. After the glue is dry, insert the assembly into the ½ inch PVC T-coupling so the screen is on the inside of the coupling. Push on the assembly to ensure a tight fit.

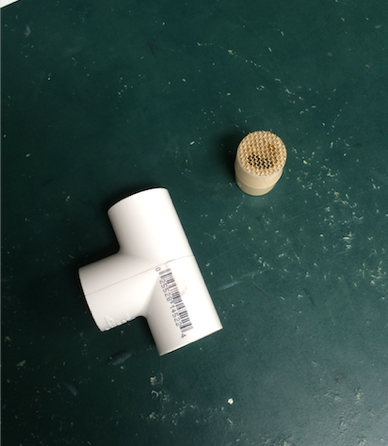
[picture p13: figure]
../../../../Desktop/Picture1%202.pn
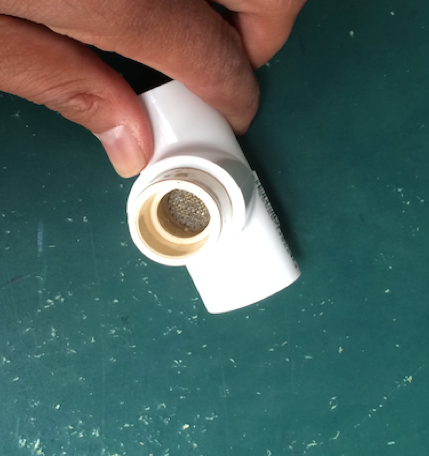
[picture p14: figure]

3. Unscrew the lid of the ½ inch PVC T-conduit and super glue the zinc-plated fender washer such that the washer hole is centered over the T-conduit hole. See picture on next page.

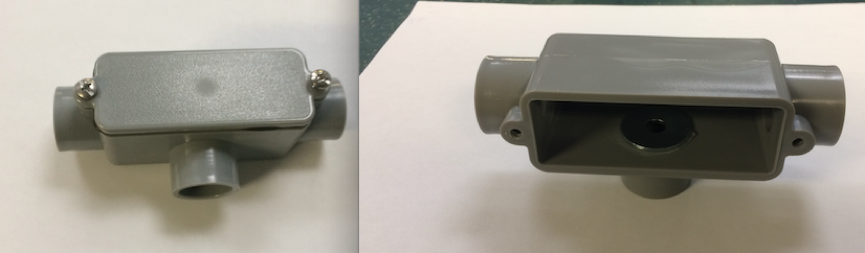
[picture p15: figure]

4. Insert the ½ inch PVC 90° elbow into the T-conduit. The flared end of the 90° elbow should be pointing towards the ground, as should the hole in the T-conduit with the washer.

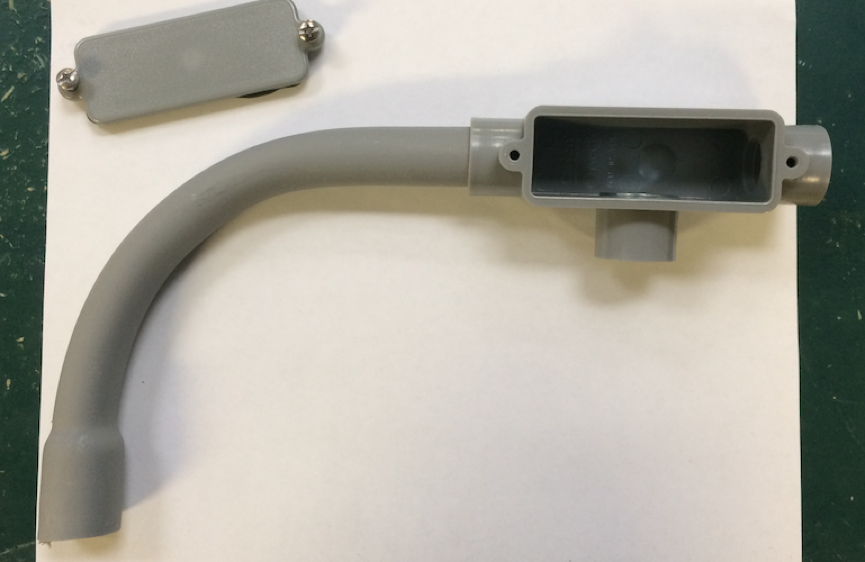
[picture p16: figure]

5. Insert the assembly from step 2 to the open end of T-conduit opposite of the 90° elbow.

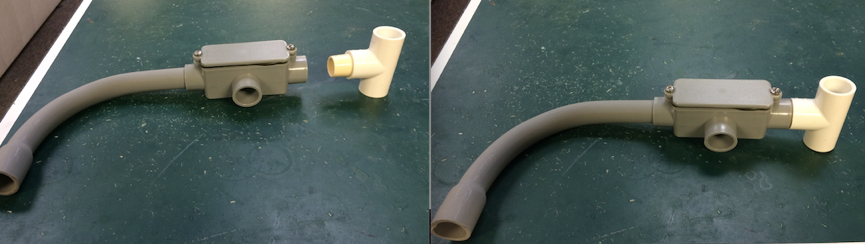
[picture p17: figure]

6. Solder the IR sensor to the multi-strand wire and super glue the rubber washer to the PCB. The rubber washer should fit around the metal can of the sensor. Ensure the lens is protruding past the plane of the washer to avoid reading interference. Avoid getting super glue on the lens. See image on the next page.

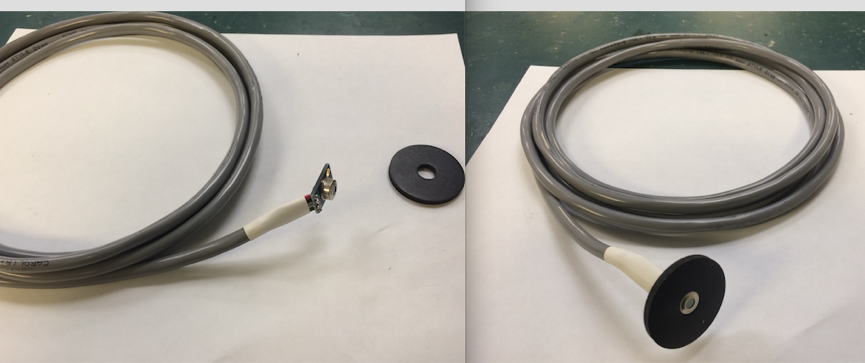
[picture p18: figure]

7. Insert the free end of the wire through the opening at the bottom of the T-conduit and through the 90° PVC elbow.

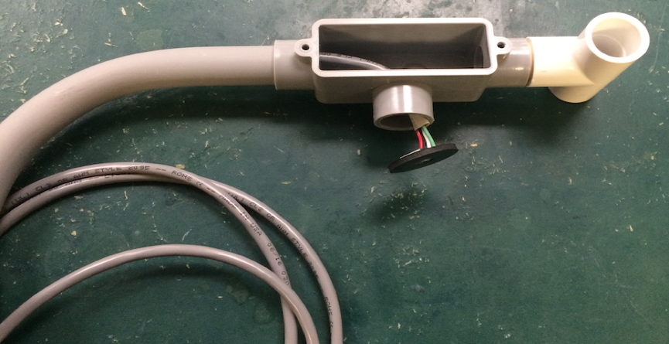
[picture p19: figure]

8. Glue the rubber washer to the T-conduit and zip tie the wire to the 90° elbow for strain relief.

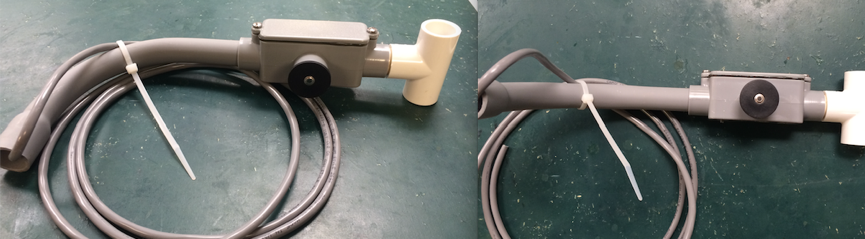
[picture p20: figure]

Usage Information

Using a hose clamp, attach the MLX90614 housing to the LEMS t-post, or to whatever is available. Visually ensure that nothing but ground is in the field of view of MLX90614 sensor.

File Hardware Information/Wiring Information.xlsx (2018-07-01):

Connections are to be made from node to node going left to right via edges
When referring to left (LHS) or right (RHS) of the LEMS shield, the SD Card connector is on top
SHT31: | Use gray 4-wire multi-strand cable for connections
VIN | Solder | Red Sub-Wire | Screw | "3.3V" on RHS of LEMS Shield
GND | Solder | Black Sub-Wire | Screw | "GND" on RHS of LEMS Shield
SCL | Solder | White Sub-Wire | Screw | "SCL" on RHS of LEMS Shield
SDA | Solder | Green Sub-Wire | Screw | "SDA" on RHS of LEMS Shield
MLX90614: | Use gray 4-wire multi-strand cable for connections
VIN | Solder | Red Sub-Wire | Screw | "3.3V" on RHS of LEMS Shield
GND | Solder | Black Sub-Wire | Screw | "GND" on RHS of LEMS Shield
SCL | Solder | White Sub-Wire | Screw | "SCL" on RHS of LEMS Shield
SDA | Solder | Green Sub-Wire | Screw | "SDA" on RHS of LEMS Shield
Li200R: | No intermediate wire necessary. Note: Different Li200s have different wiring. The two configurations are below
Blue | Screw | "LI+" on LHS of LEMS Shield
Brown+Shield | Screw | "LI-" on LHS of LEMS Shield
OR
Shield | Screw | "Li+" on LHS of LEMS Shield
Copper | Screw | "Li-" on LHS of LEMS Shield
Davis Anemometer: | No intermediate wire necessary
Black | Screw | "WIND SPD" on RHS of LEMS Shield
Red | Screw | "WIND GND" on RHS of LEMS Shield
Green | Screw | "WIND DIR" on RHS of LEMS Shield
Yellow | Screw | "WIND POW" on RHS of LEMS Shield
Upper Soil (5TM): | No intermediate wire necessary. Note: Two sensors present, either wiring configuration possible
Bare/Shield | Screw | "U5TM GND" on LHS of LEMS Shield
Red | Screw | "U5TM DATA" on LHS of LEMS Shield
White | Screw | "U5TM POW" on LHS of LEMS Shield
OR
Bare/Shield | Screw | "U5TM GND" on LHS of LEMS Shield
Orange | Screw | "U5TM DATA" on LHS of LEMS Shield
Brown | Screw | "U5TM POW" on LHS of LEMS Shield
Lower Soil (5TM): | No intermediate wire necessary. Note: Two sensors present, either wiring configuration possible
Bare/Shield | Screw | "L5TM GND" on RHS of LEMS Shield
Red | Screw | "L5TM DATA" on RHS of LEMS Shield
White | Screw | "L5TM POW" on RHS of LEMS Shield
OR
Bare/Shield | Screw | "L5TM GND" on RHS of LEMS Shield
Orange | Screw | "L5TM DATA" on RHS of LEMS Shield
Brown | Screw | "L5TM POW" on RHS of LEMS Shield
DS2 Anemometer/Atmos 22 Anemometer: | No itermediate wire necessary. Note: This anemometer changed in 2018, so there are two names and two different wiring schemes (as seen below)
Bare/Shield | Screw | "GND" on LHS of LEMS Shield
Red | Screw | "SONIC DATA" on LHS of LEMS Shield
White | Screw | "5V" on LHS of LEMS Shield
OR
Bare/Shield | Screw | "GND" on LHS of LEMS Shield
Orange | Screw | "SONIC DATA" on LHS of LEMS Shield
Brown | Screw | "5V" on LHS of LEMS Shield

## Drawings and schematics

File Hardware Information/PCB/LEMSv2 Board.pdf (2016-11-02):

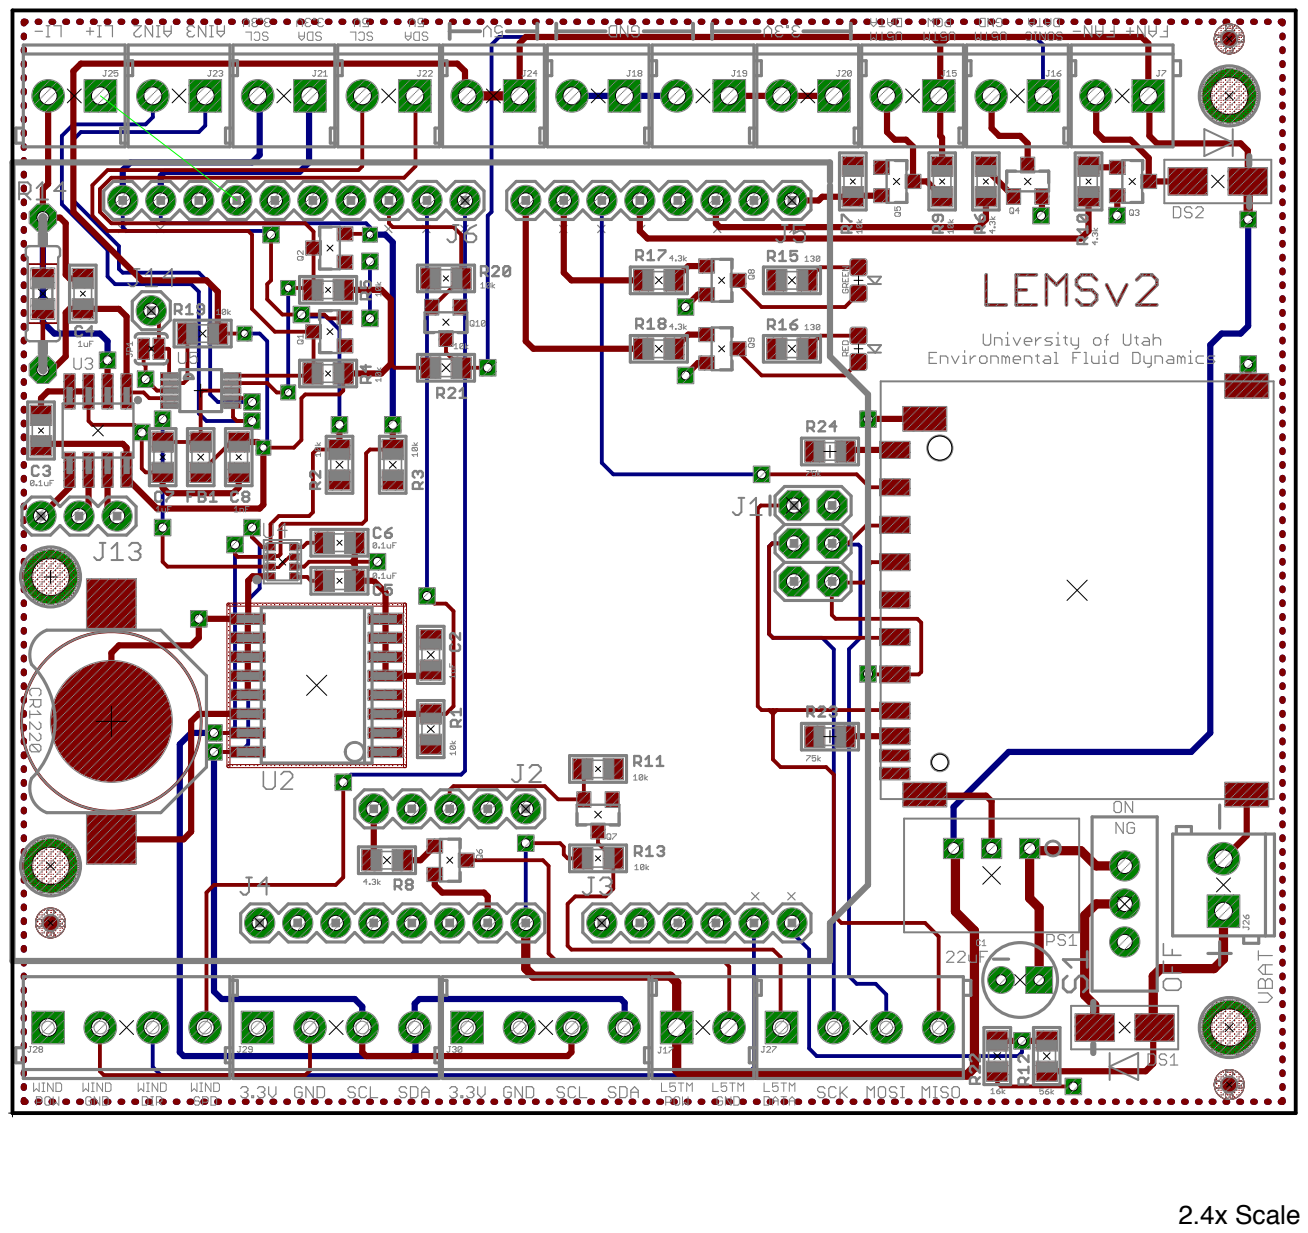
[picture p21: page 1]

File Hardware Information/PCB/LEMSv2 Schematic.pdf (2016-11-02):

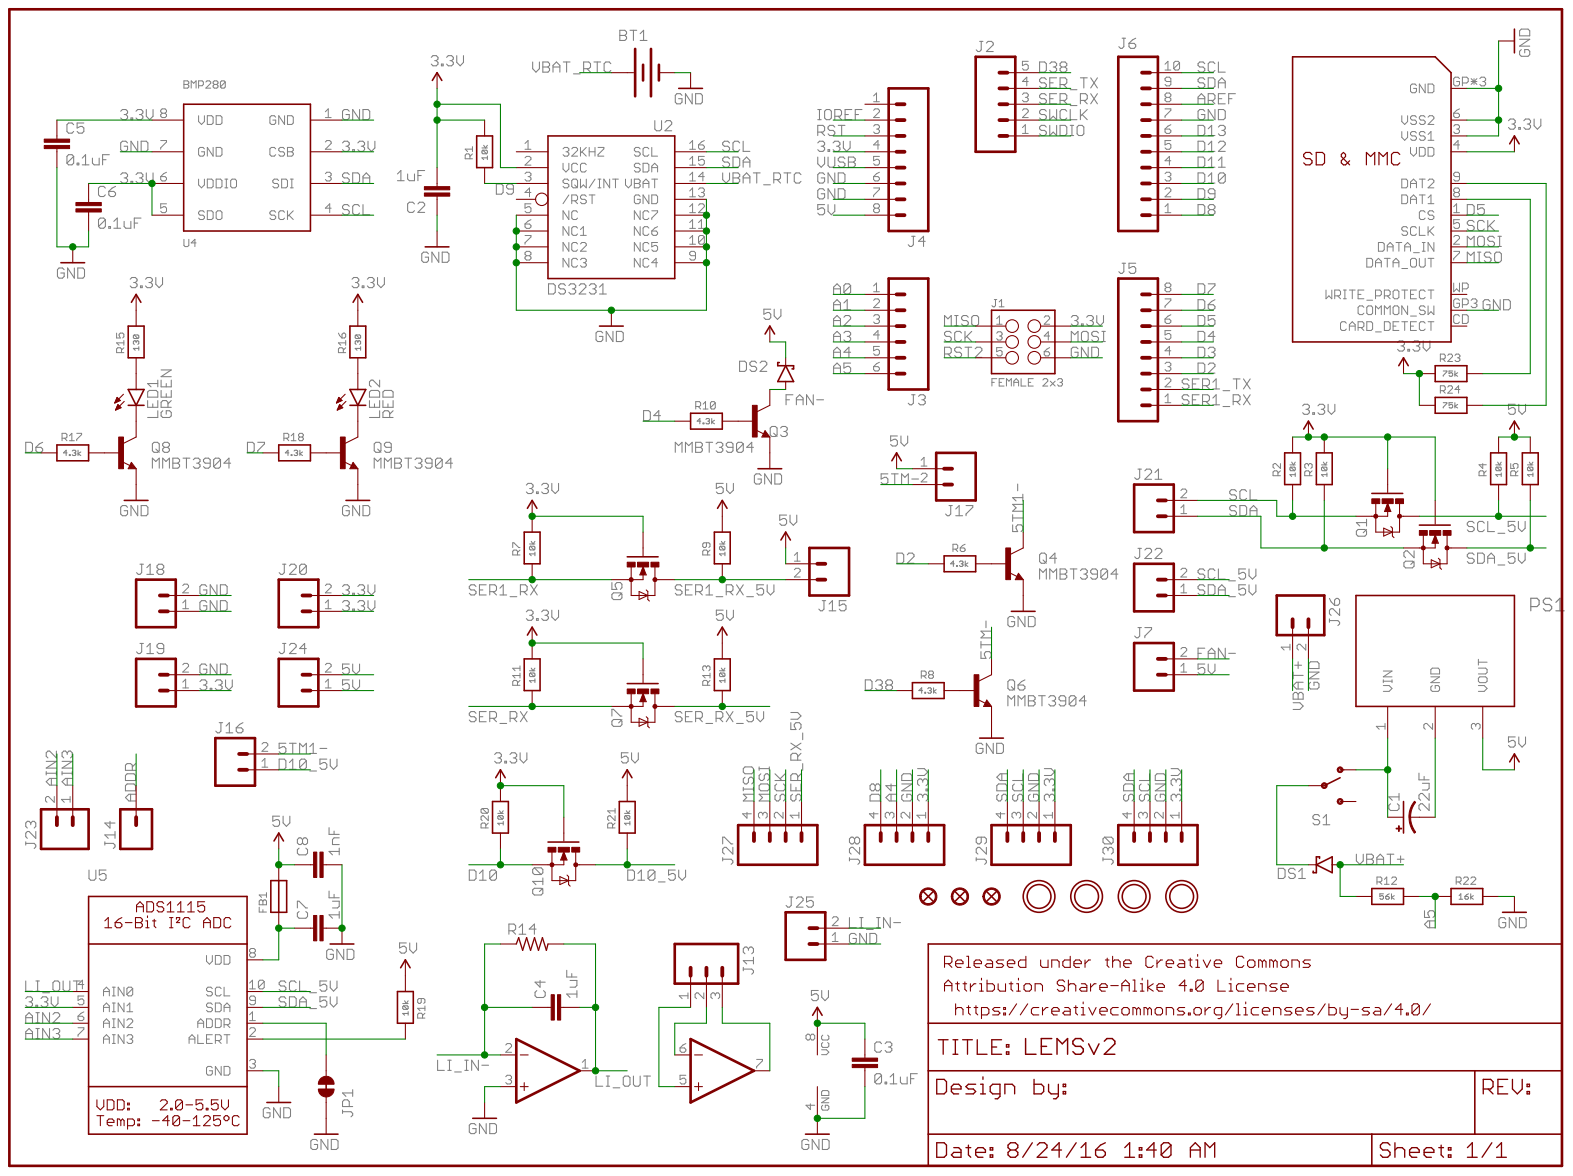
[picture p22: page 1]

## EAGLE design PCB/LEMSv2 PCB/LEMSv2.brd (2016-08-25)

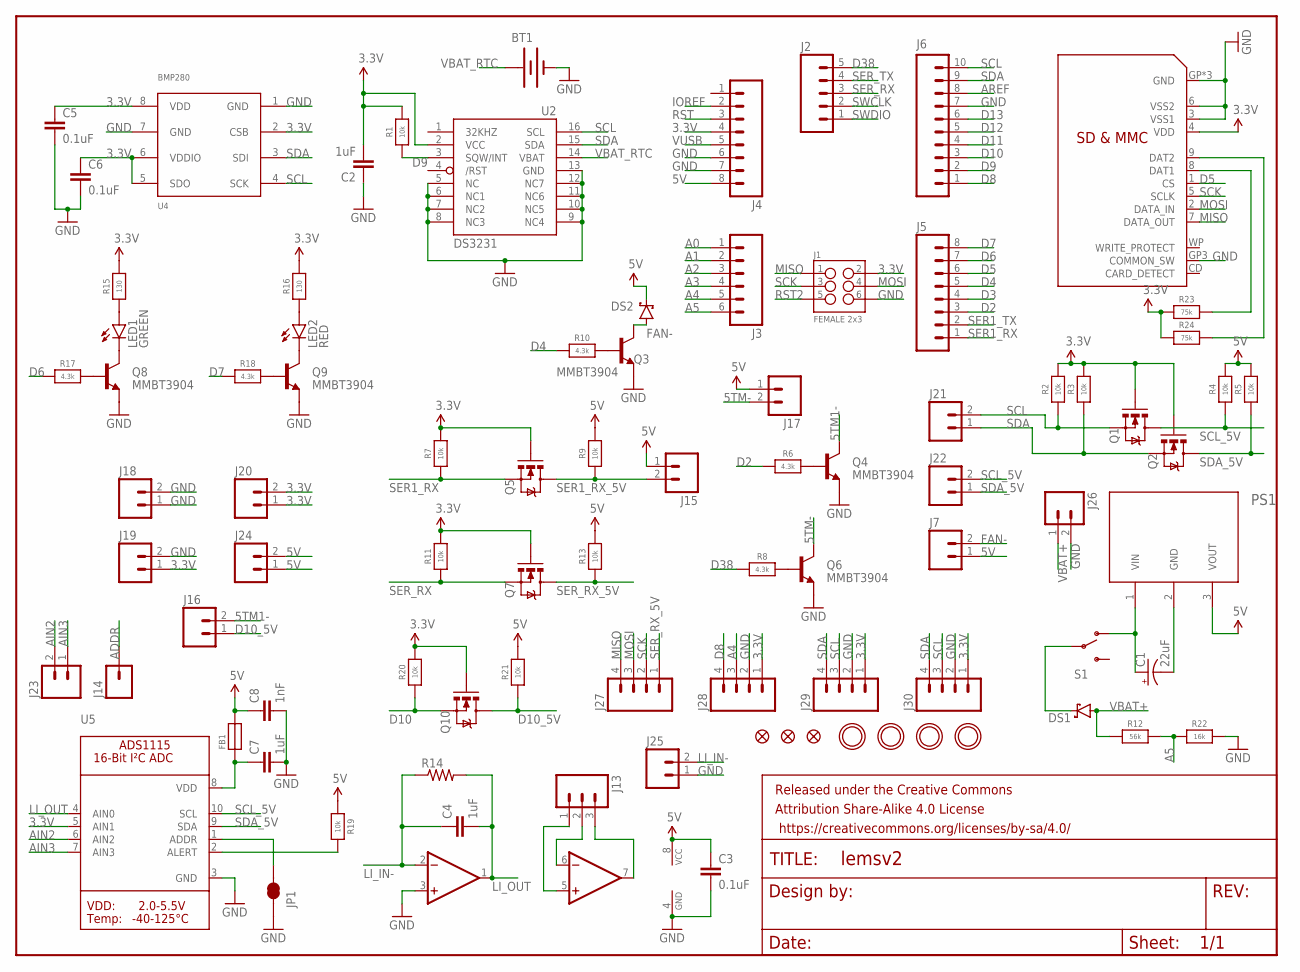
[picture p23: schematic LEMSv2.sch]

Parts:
BT1: BATTERY12MM; BATTCON_12MM
C1: 22uF; CPOL-RADIAL-10UF-25V
C2, C4, C7: 1uF; _0805
C3, C5, C6: 0.1uF; _0805
C8: 1nF; _0805
DS1, DS2: DIODE_SCHOTTKY; DO-214AC
FB1: FERRITE; _0805
FID1, FID2, FID3: FIDUCIAL""; FIDUCIAL_1MM
FRAME1: FRAME-LETTERNO_PACKAGE; DUMMY
J1: FEMALE 2x3; 2X3
J2: M05PTH; 1X05
J3: M06SILK_FEMALE_PTH; 1X06
J4, J5: M08; 1X08_ROUND
J6: M10SILK_FEMALE_PTH; 1X10
J7, J15, J16, J17, J18, J19, J20, J21, J22, J23, J24, J25, J26: M023.5MM; SCREWTERMINAL-3.5MM-2
J13: M03PTH; 1X03
J14: M01PTH; 1X01
J27, J28, J29, J30: M04SCREW; SCREWTERMINAL-3.5MM-4
JP1: JUMPER-PAD-2-NC_BY_TRACE; PAD-JUMPER-2-NC_BY_TRACE_YES_SILK
LED1: GREEN; LED-0603
LED2: RED; LED-0603
PS1: TSR_1-2450
Q1, Q2, Q5, Q7, Q10: 200mA/50V; SOT23-3
Q3, Q4, Q6, Q8, Q9: MMBT3904; SOT23-3
R1, R2, R3, R4, R5, R7, R9, R11, R13, R19, R20, R21: 10k; _0805
R6, R8, R10, R17, R18: 4.3k; _0805
R12: 56k; _0805
R14: R-US_FLIPFLOP; 0805-THM
R15, R16: 130; _0805
R22: 16k; _0805
R23, R24: 75k; _0805
S1: SWITCH-SPDTPTH; SWITCH-SPDT
U1: SDMMC06132; 06132
U2: DS3231/SO; SO16W
U3: TLV2372; SOIC8
U4: BMP280
U5: ADC_ADS1115; MSOP10
U$1, U$2, U$3, U$4: MOUNTINGHOLE2.5; MOUNTINGHOLE_2.5_PLATED

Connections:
3.3V: C2.2, C5.1, C6.1, J1.2, J4.4, J19.1, J20.1, J20.2, J28.1, J29.1, J30.1, Q1.1 (G), Q2.1 (G), Q5.1 (G), Q7.1 (G), Q10.1 (G), R1.2, R2.2, R3.2, R7.2, R11.2, R15.2, R16.2, R20.2, R23.1, R24.1, U1.4 (VDD), U2.2 (VCC), U4.2 (CSB), U4.5 (SDO), U4.6 (VDDIO), U4.8 (VDD), U5.5 (AIN1)
5TM1-: J16.2, Q4.3 (C)
5TM-: J17.2, Q6.3 (C)
5V: C3.1, C8.1, DS2.C, FB1.2, J4.8, J7.1, J15.1, J17.1, J24.1, J24.2, PS1.3 (VOUT), R4.2, R5.2, R9.2, R13.2, R19.1, R21.2, U3.8 (VCC)
A0: J3.1
A1: J3.2
A2: J3.3
A3: J3.4
A4: J3.5, J28.3
A5: J3.6, R12.2, R22.1
ADDR: J14.1, JP1.1, U5.1 (ADDR)
AIN2: J23.2, U5.6 (AIN2)
AIN3: J23.1, U5.7 (AIN3)
ALERT: R19.2, U5.2 (ALERT)
AREF: J6.8
D2: J5.3, R6.1
D3: J5.4
D4: J5.5, R10.1
D5: J5.6, U1.1 (CS)
D6: J5.7, R17.1
D7: J5.8, R18.1
D8: J6.1, J28.4
D9: J6.2, R1.1, U2.3 (SQW/INT)
D10: J6.3, Q10.2 (S), R20.1
D10_5V: J16.1, Q10.3 (D), R21.1
D11: J6.4
D12: J6.5
D13: J6.6
D38: J2.5, R8.1
FAN-: DS2.A, J7.2, Q3.3 (C)
GND: BT1.GND (-), C1.2 (-), C2.1, C3.2, C5.2, C6.2, C7.2, C8.2, J1.6, J4.6, J4.7, J6.7, J18.1, J18.2, J19.2, J25.1, J26.2, J28.2, J29.2, J30.2, JP1.2, PS1.2 (GND), Q3.2 (E), Q4.2 (E), Q6.2 (E), Q8.2 (E), Q9.2 (E), R22.2, U1.3 (VSS1), U1.6 (VSS2), U1.GP (GND), U1.GP2 (GND), U1.GP3 (COMMON_SW), U1.GP4 (GND), U2.5 (NC), U2.6 (NC1), U2.7 (NC2), U2.8 (NC3), U2.9 (NC4), U2.10 (NC5), U2.11 (NC6), U2.12 (NC7), U2.13 (GND), U3.3 (+IN), U3.4 (GND), U4.1 (GND), U4.7 (GND), U5.3 (GND)
IOREF: J4.2
LI_IN-: C4.1, J25.2, R14.1, U3.2 (-IN)
LI_OUT: C4.2, R14.2, U3.1 (OUT), U5.4 (AIN0)
MISO: J1.1, J27.4, U1.7 (DATA_OUT)
MOSI: J1.4, J27.3, U1.2 (DATA_IN)
unnamed: C1.1 (+), PS1.1 (VIN), S1.1 (O)
unnamed: J13.2, U3.6 (-IN)
unnamed: J13.1, U3.5 (+IN)
unnamed: J13.3, U3.7 (OUT)
unnamed: Q8.1 (B), R17.2
unnamed: Q9.1 (B), R18.2
unnamed: LED1.C, Q8.3 (C)
unnamed: LED2.C, Q9.3 (C)
unnamed: LED1.A, R15.1
unnamed: LED2.A, R16.1
unnamed: Q4.1 (B), R6.2
unnamed: Q6.1 (B), R8.2
unnamed: DS1.C, S1.2
unnamed: C7.1, FB1.1, U5.8 (VDD)
unnamed: Q3.1 (B), R10.2
unnamed: R23.2, U1.8 (DAT1)
unnamed: R24.2, U1.9 (DAT2)
RST: J4.3
RST2: J1.5
SCK: J1.3, J27.2, U1.5 (SCLK)
SCL: J6.10, J21.2, J29.3, J30.3, Q1.2 (S), R2.1, U2.16 (SCL), U4.4 (SCK)
SCL_5V: J22.2, Q1.3 (D), R4.1, U5.10 (SCL)
SDA: J6.9, J21.1, J29.4, J30.4, Q2.2 (S), R3.1, U2.15 (SDA), U4.3 (SDI)
SDA_5V: J22.1, Q2.3 (D), R5.1, U5.9 (SDA)
SER1_RX: J5.1, Q5.2 (S), R7.1
SER1_RX_5V: J15.2, Q5.3 (D), R9.1
SER1_TX: J5.2
SER_RX: J2.3, Q7.2 (S), R11.1
SER_RX_5V: J27.1, Q7.3 (D), R13.1
SER_TX: J2.4
SWCLK: J2.2
SWDIO: J2.1
VBAT+: DS1.A, J26.1, R12.1
VBAT_RTC: BT1.PWR@1 (+), U2.14 (VBAT)
VUSB: J4.5

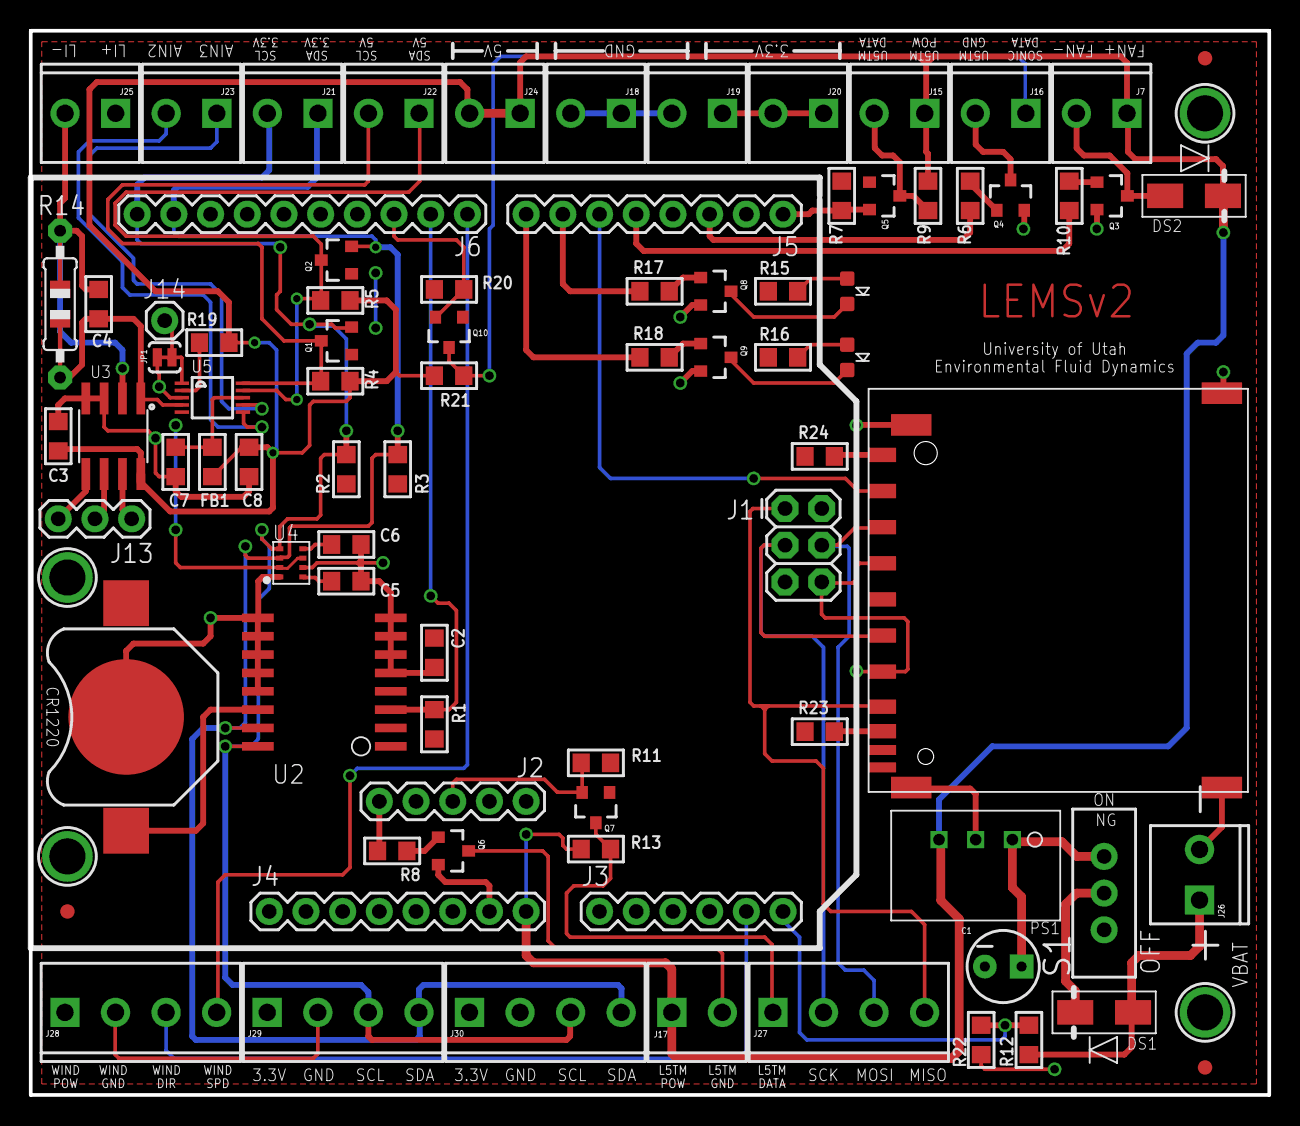
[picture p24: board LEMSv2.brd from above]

Board: 2 copper layers, 85.7 x 73.7 mm, 89 parts (0 on the bottom side), 54 nets.

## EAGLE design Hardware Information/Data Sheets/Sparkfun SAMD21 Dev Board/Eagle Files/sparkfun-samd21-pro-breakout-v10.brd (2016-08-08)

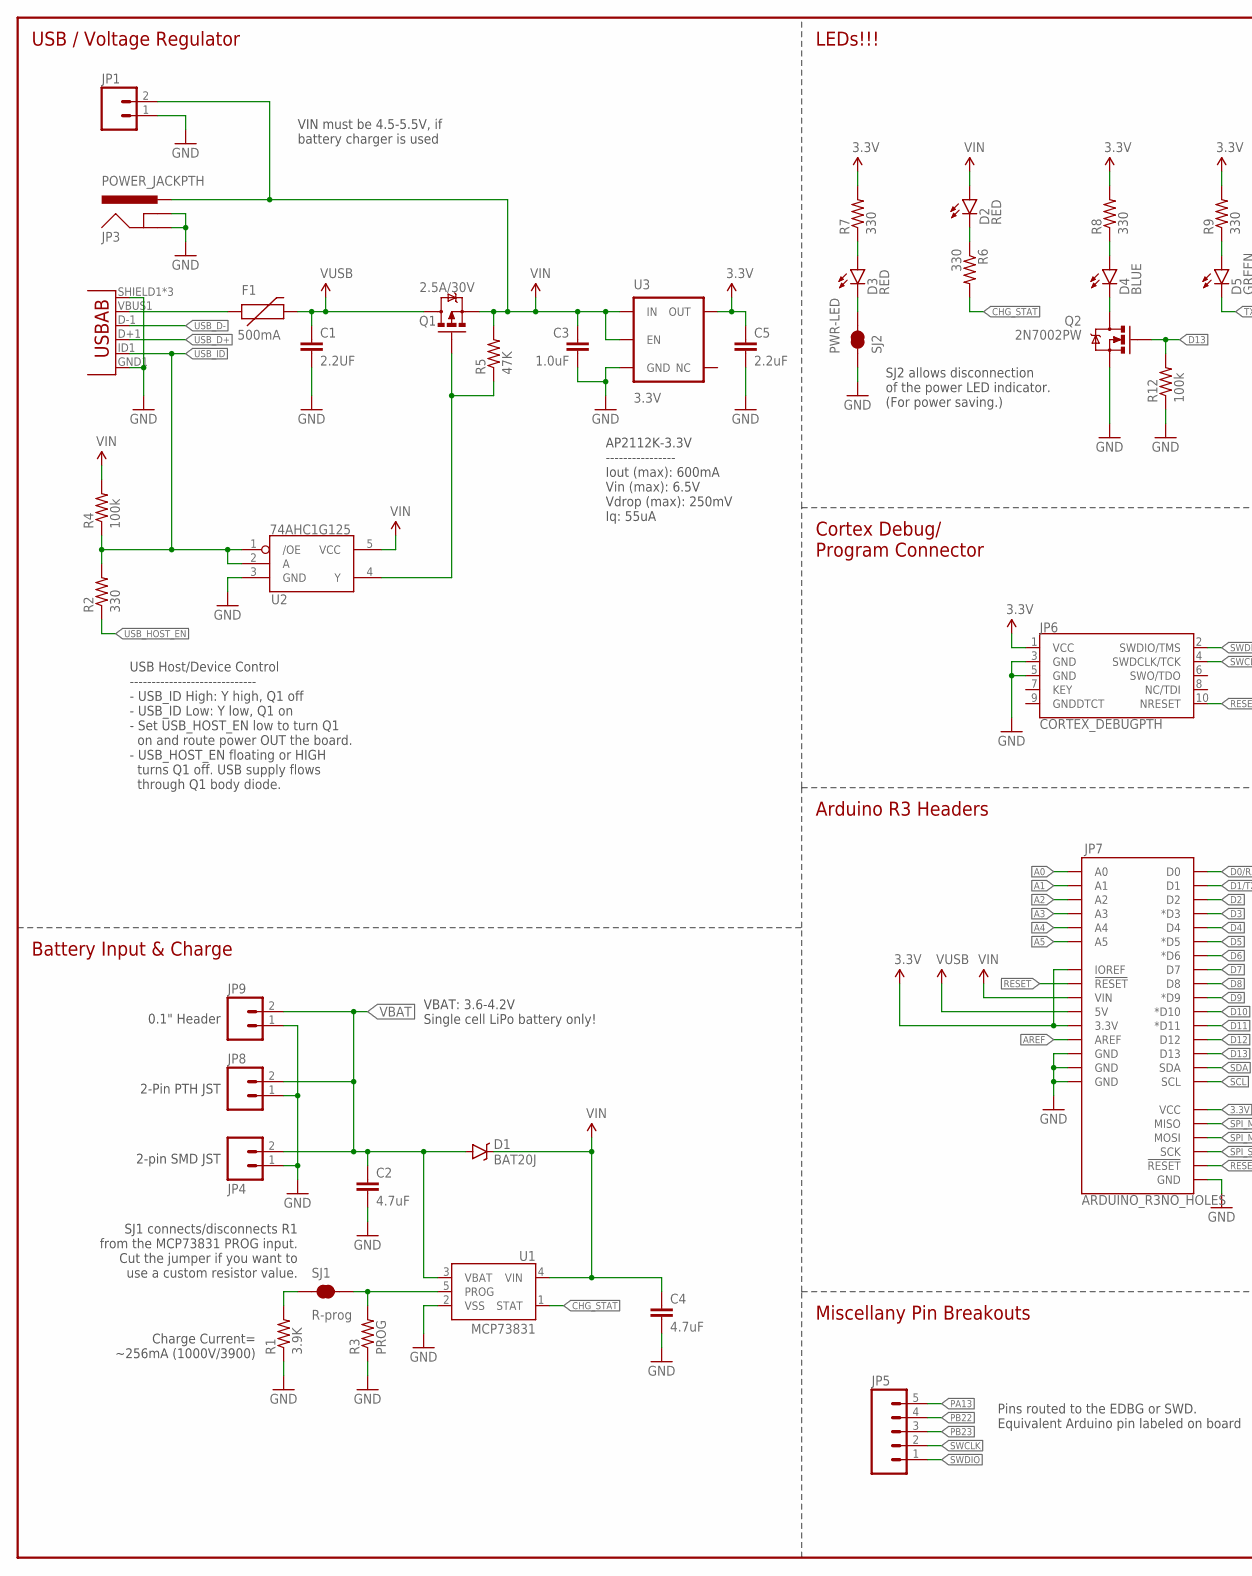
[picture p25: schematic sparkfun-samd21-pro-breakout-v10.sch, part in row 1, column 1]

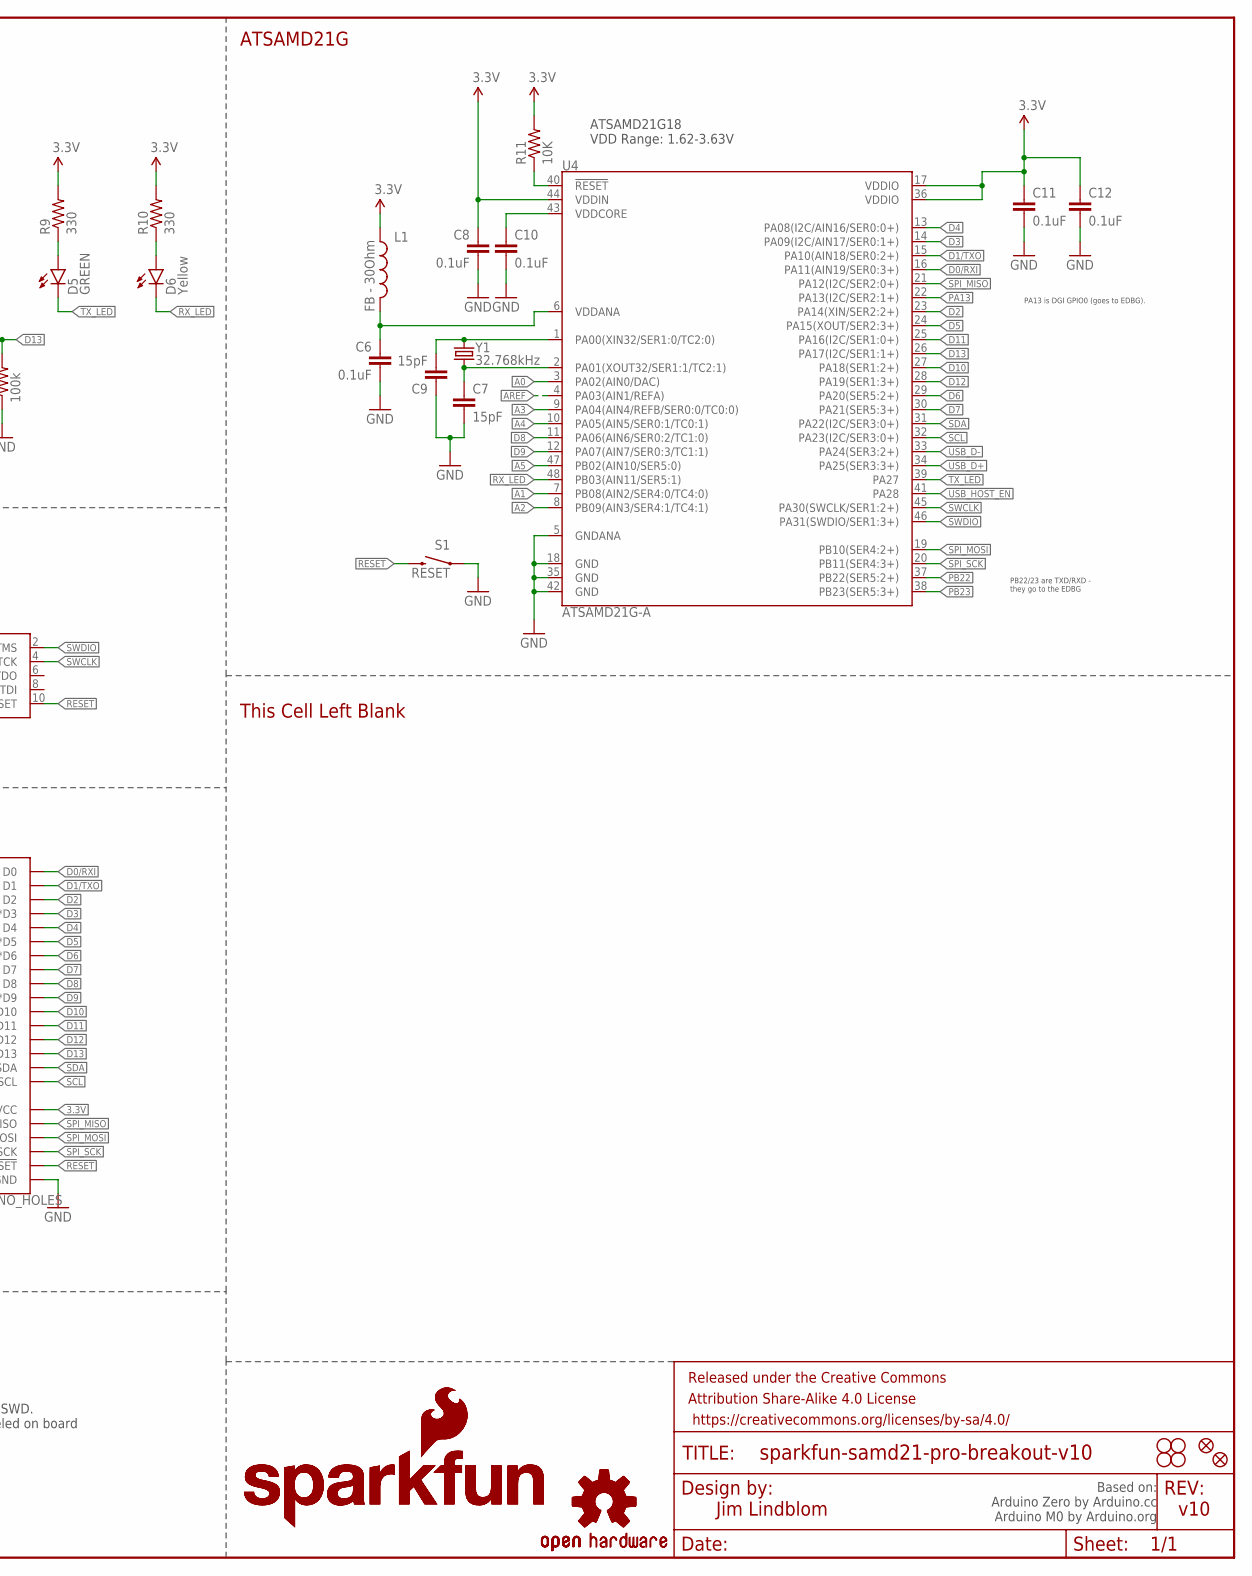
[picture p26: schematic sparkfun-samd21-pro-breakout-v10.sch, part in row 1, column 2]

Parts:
C1: 2.2UF; 1206
C2, C4: 4.7uF; 0603-CAP
C3: 1.0uF; 0805-CAP
C5: 2.2uF; 0603-CAP
C6, C8, C10, C11, C12: 0.1uF; 0603-CAP
C7, C9: 15pF; 0603-CAP
D1: BAT20J; SOD-323
D2, D3: RED; LED-0603
D4: BLUE; LED-0603
D5: GREEN; LED-0603
D6: Yellow; LED-0603
F1: 500mA; PTC-1206
FID1, FID2: FIDUCIAL1X2; FIDUCIAL-1X2
FRAME1: FRAME-LEDGER; CREATIVE_COMMONS
JP1: M02PTH; 1X02
JP2: USB-ABCONN-11794; USB-AB-MICRO-SMD_V03
JP3: POWER_JACKPTH; POWER_JACK_PTH
JP4: M02-JST-2MM-SMT; JST-2-SMD
JP5: M05NO_SILK; 1X05_NO_SILK
JP6: CORTEX_DEBUGPTH; 2X5-PTH-1.27MM
JP7: ARDUINO_R3NO_HOLES; ARDUINO_R3_NO_HOLES
JP8: M02-JST-2-PTH-NO_SILK; JST-2-PTH-NS
JP9: M021X02_NO_SILK; 1X02_NO_SILK
L1: FB - 30Ohm; 0603
LOGO1: SFE_LOGO_NAME_FLAME.2_INCH; SFE_LOGO_NAME_FLAME_.2
LOGO2: SFE_LOGO_NAME_FLAME.4_INCH; SFE_LOGO_NAME_FLAME_.4
LOGO3: OSHW-LOGOS; OSHW-LOGO-S
LOGO4: OSHW-LOGOL; OSHW-LOGO-L
Q1: 2.5A/30V; SOT23-3
Q2: 2N7002PW; SOT323
R1: 3.9K; 0603
R2, R6, R7, R8, R9, R10: 330; 0603-RES
R3: PROG; 1/6W-RES
R4, R12: 100k; 0603-RES
R5: 47K; 0603-RES
R11: 10K; 0603-RES
S1: RESET; TACTILE-SWITCH-SMD
SJ1: R-prog; PAD-JUMPER-2-NC_BY_TRACE_YES_SILK
SJ2: PWR-LED; PAD-JUMPER-2-NC_BY_TRACE_NO_SILK
STANDOFF1, STANDOFF2, STANDOFF3, STANDOFF4: STAND-OFF
U1: MCP73831; SOT23-5
U2: 74AHC1G125; SOT23-5
U3: 3.3V; SOT23-5
U4: ATSAMD21G-A; TQFP-48
Y1: 32.768kHz; CRYSTAL-SMD-3.2X1.5MM

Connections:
3.3V: C5.1, C8.1, C11.1, C12.1, JP6.1 (VCC), JP7.3.3V, JP7.IOREF, JP7.VCC, L1.1, R7.2, R8.2, R9.2, R10.2, R11.2, U3.5 (OUT), U4.17 (VDDIO), U4.36 (VDDIO), U4.44 (VDDIN)
!RESET: JP6.10 (NRESET), JP7.RESET@1 (!RESET!), JP7.RESET@2 (!RESET!), R11.1, S1.3 (2), U4.40 (!RESET!)
A0: JP7.A0, U4.3 (PA02(AIN0/DAC))
A1: JP7.A1, U4.7 (PB08(AIN2/SER4:0/TC4:0))
A2: JP7.A2, U4.8 (PB09(AIN3/SER4:1/TC4:1))
A3: JP7.A3, U4.9 (PA04(AIN4/REFB/SER0:0/TC0:0))
A4: JP7.A4, U4.10 (PA05(AIN5/SER0:1/TC0:1))
A5: JP7.A5, U4.47 (PB02(AIN10/SER5:0))
AREF: JP7.AREF, U4.4 (PA03(AIN1/REFA))
CHG_STAT: R6.2, U1.1 (STAT)
D0/RXI: JP7.D0, U4.16 (PA11(AIN19/SER0:3+))
D1/TXO: JP7.D1, U4.15 (PA10(AIN18/SER0:2+))
D2: JP7.D2, U4.23 (PA14(XIN/SER2:2+))
D3: JP7.D3 (*D3), U4.14 (PA09(I2C/AIN17/SER0:1+))
D4: JP7.D4, U4.13 (PA08(I2C/AIN16/SER0:0+))
D5: JP7.D5 (*D5), U4.24 (PA15(XOUT/SER2:3+))
D6: JP7.D6 (*D6), U4.29 (PA20(SER5:2+))
D7: JP7.D7, U4.30 (PA21(SER5:3+))
D8: JP7.D8, U4.11 (PA06(AIN6/SER0:2/TC1:0))
D9: JP7.D9 (*D9), U4.12 (PA07(AIN7/SER0:3/TC1:1))
D10: JP7.D10 (*D10), U4.27 (PA18(SER1:2+))
D11: JP7.D11 (*D11), U4.25 (PA16(I2C/SER1:0+))
D12: JP7.D12, U4.28 (PA19(SER1:3+))
D13: JP7.D13, Q2.1 (G), R12.2, U4.26 (PA17(I2C/SER1:1+))
GND: C1.2, C2.2, C3.2, C4.2, C5.2, C6.2, C7.2, C8.2, C9.1, C10.2, C11.2, C12.2, JP1.1, JP2.GND1 (GND), JP2.SHIELD1 (SHIELD), JP2.SHIELD2 (SHIELD), JP2.SHIELD3 (SHIELD), JP3.GND, JP3.GNDBREAK, JP4.1 (2), JP6.3 (GND), JP6.5 (GND), JP7.GND@1 (GND), JP7.GND@2 (GND), JP7.GND@3 (GND), JP7.GND@4 (GND), JP8.1, JP9.1, Q2.2 (S), R1.1, R3.1, R12.1, S1.1, SJ2.1, U1.2 (VSS), U2.3 (GND), U3.2 (GND), U4.5 (GNDANA), U4.18 (GND), U4.35 (GND), U4.42 (GND)
unnamed: F1.1, JP2.VBUS1 (VBUS)
unnamed: C9.2, U4.1 (PA00(XIN32/SER1:0/TC2:0)), Y1.P$2 (2)
unnamed: D4.C, Q2.3 (D)
unnamed: C7.1, U4.2 (PA01(XOUT32/SER1:1/TC2:1)), Y1.P$1 (1)
unnamed: D3.A, R7.1
unnamed: D4.A, R8.1
unnamed: D2.C, R6.1
unnamed: D5.A, R9.1
unnamed: D6.A, R10.1
unnamed: D3.C, SJ2.2
unnamed: R1.2, SJ1.1
unnamed: R3.2, SJ1.2, U1.5 (PROG)
PA13: JP5.5, U4.22 (PA13(I2C/SER2:1+))
PB22: JP5.4, U4.37 (PB22(SER5:2+))
PB23: JP5.3, U4.38 (PB23(SER5:3+))
RX_LED: D6.C, U4.48 (PB03(AIN11/SER5:1))
SCL: JP7.SCL, U4.32 (PA23(I2C/SER3:0+))
SDA: JP7.SDA, U4.31 (PA22(I2C/SER3:0+))
SPI_MISO: JP7.MISO, U4.21 (PA12(I2C/SER2:0+))
SPI_MOSI: JP7.MOSI, U4.19 (PB10(SER4:2+))
SPI_SCK: JP7.SCK, U4.20 (PB11(SER4:3+))
SWCLK: JP5.2, JP6.4 (SWDCLK/TCK), U4.45 (PA30(SWCLK/SER1:2+))
SWDIO: JP5.1, JP6.2 (SWDIO/TMS), U4.46 (PA31(SWDIO/SER1:3+))
TX_LED: D5.C, U4.39 (PA27)
USB_D+: JP2.D+1 (D+), U4.34 (PA25(SER3:3+))
USB_D-: JP2.D-1 (D-), U4.33 (PA24(SER3:2+))
USB_HOST_EN: R2.1, U4.41 (PA28)
USB_HOST_POWER_EN: Q1.1 (G), R5.1, U2.4 (Y)
USB_ID: JP2.ID1 (USBID), R2.2, R4.1, U2.1 (/OE), U2.2 (A)
VBAT: C2.1, D1.A, JP4.2 (1), JP8.2, JP9.2, U1.3 (VBAT)
VDDANA: C6.1, L1.2, U4.6 (VDDANA)
VDDCORE: C10.1, U4.43 (VDDCORE)
VIN: C3.1, C4.1, D1.C, D2.A, JP1.2, JP3.PWR, JP7.VIN, Q1.2 (S), R4.2, R5.2, U1.4 (VIN), U2.5 (VCC), U3.1 (IN), U3.3 (EN)
VUSB: C1.1, F1.2, JP7.5V, Q1.3 (D)

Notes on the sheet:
PB22/23 are TXD/RXD - they go to the EDBG
PA13 is DGI GPIO0 (goes to EDBG).
USB / Voltage Regulator
LEDs!!!
Cortex Debug/ Program Connector
Arduino R3 Headers
ATSAMD21G
Jim Lindblom
v10
Charge Current= ~256mA (1000V/3900)
SJ1 connects/disconnects R1 from the MCP73831 PROG input. Cut the jumper if you want to use a custom resistor value.
Battery Input & Charge
SJ2 allows disconnection of the power LED indicator. (For power saving.)
Miscellany Pin Breakouts
This Cell Left Blank
VIN must be 4.5-5.5V, if battery charger is used
ATSAMD21G18 VDD Range: 1.62-3.63V
Based on: Arduino Zero by Arduino.cc Arduino M0 by Arduino.org
0.1" Header
2-Pin PTH JST
2-pin SMD JST
AP2112K-3.3V ---------------- Iout (max): 600mA Vin (max): 6.5V Vdrop (max): 250mV Iq: 55uA
USB Host/Device Control ----------------------------- - USB_ID High: Y high, Q1 off - USB_ID Low: Y low, Q1 on - Set USB_HOST_EN low to turn Q1 on and route power OUT the board. - USB_HOST_EN floating or HIGH turns Q1 off. USB supply flows through Q1 body diode.
Pins routed to the EDBG or SWD. Equivalent Arduino pin labeled on board
VBAT: 3.6-4.2V Single cell LiPo battery only\!

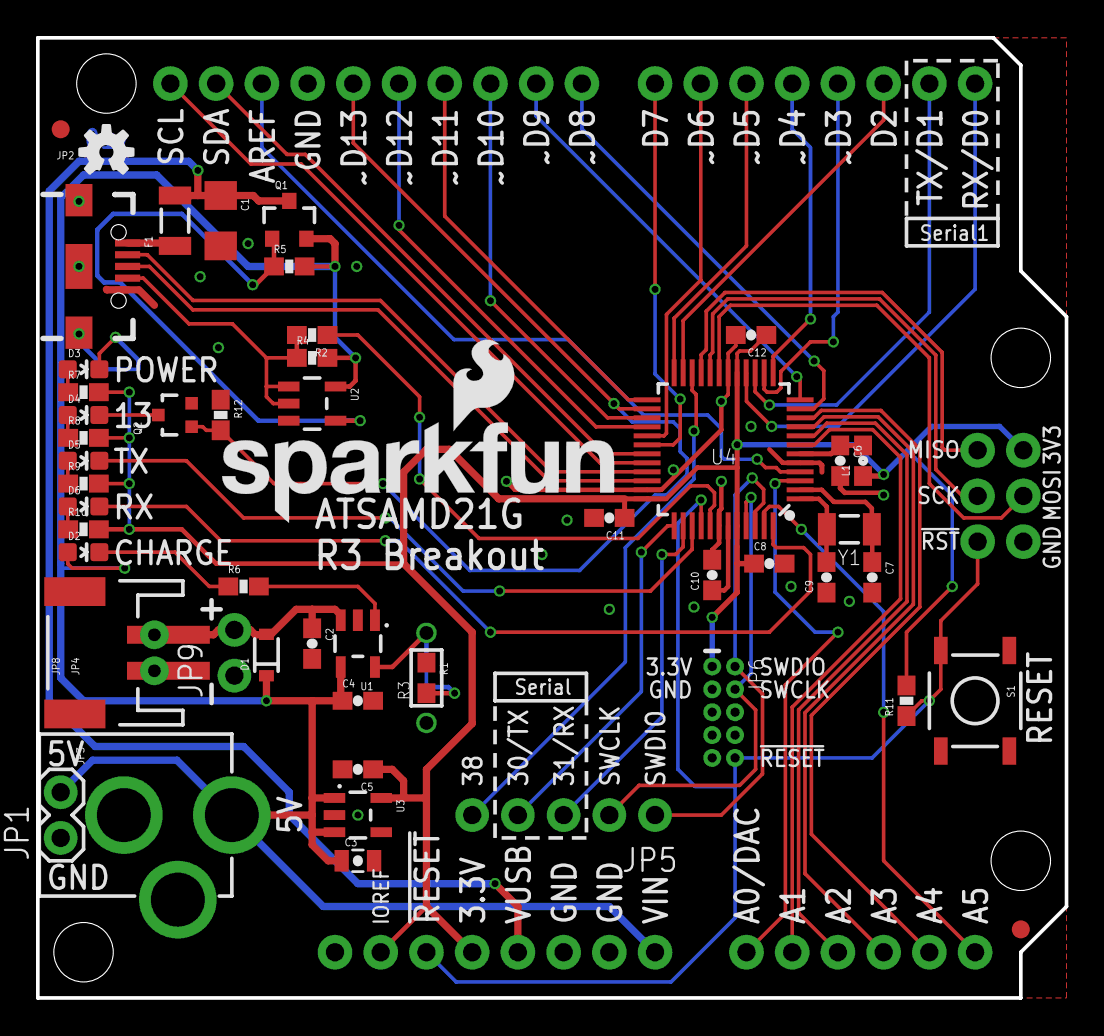
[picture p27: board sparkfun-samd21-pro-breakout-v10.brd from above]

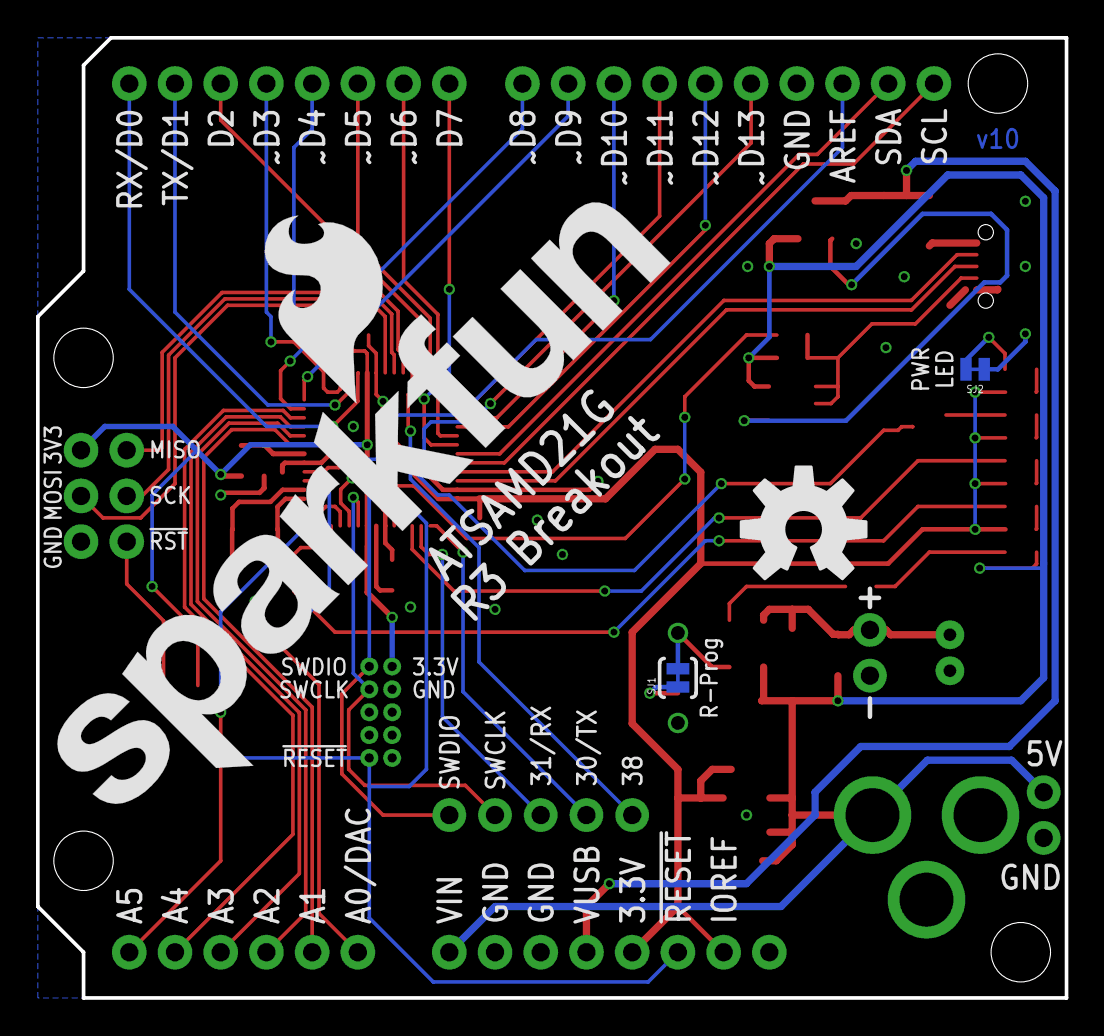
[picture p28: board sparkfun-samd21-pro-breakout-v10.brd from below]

Board: 2 copper layers, 57.1 x 53.3 mm, 62 parts (4 on the bottom side), 59 nets.

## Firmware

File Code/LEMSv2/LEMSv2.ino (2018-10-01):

// ------------------------------------------------------------------------------------------------
// Filename:
//		LEMSv2.ino
//
// Author:
//		Nipun Gunawardena
//
// Description:
//		LEMSv2 Arduino Code
//
// Credits:
//		Thanks to all the 3rd party libraries, especially to Adafruit for the excellent
//		libraries and hardware. More specifics to be added as needed
//    - Sleep code taken from https://github.com/rocketscream/Low-Power/blob/master/LowPower.cpp
//      Thanks to @sandeepmistry at https://github.com/arduino/ArduinoCore-samd/issues/142 for further help
//
// Requirements:
//		- LEMS Hardware
//		- Libraries in libraries list
//
// Notes:
//		- As far as I know, extra files have to be in the same folder as the sketch. Therefore,
//      the DS3231 alarm files have to be copied from their test folder. This means there are
//      possibilities for code divergence. Be aware.
//
// Todo:
//    - Fix battery and Licor Resistors
//
// ------------------------------------------------------------------------------------------------



// Sensor Defines: Plugged in sensors should be defined as 1 --------------------------------------
// TODO: Depreciate Wind
#define TEMPRH 1
#define IR 1
#define UPPERSOIL 1
#define LOWERSOIL 1
#define SUNLIGHT 1
#define PRESSURE 1
#define SONIC 1
#define WIND 0
#define PYRGEOMETER 0



// Other Defines ----------------------------------------------------------------------------------
// !! ALERT !! When DEBUG is defined as 0, the LEMSv2 will only work properly under battery or
// external power, NOT under USB power. If you would like to power the LEMS via USB but have DEBUG
// set to 0, uncomment the three lines centered around the line that has USBDevice.detach(); This
// should be near line 207 in the code.
#define DEBUG 0



// Pin Defines ------------------------------------------------------------------------------------
#define GREEN_LED_PIN 6     // Green LED pin
#define RED_LED_PIN 7       // Red LED pin
#define BLUE_LED_PIN 13     // Built-in Blue LED - Sparkfun SAMD21 Dev Board

#define CARDSELECT 5        // SD  card chip select pin
#define RTC_ALARM_PIN 9     // DS3231 Alarm pin
#define BAT_PIN A5          // Battery resistor div. pin
#define FAN_PIN 11          // Pin for cooling fan

#define WDIR_PIN A4         // Davis wind direction pin
#define WSPD_PIN 8          // Davis wind speed pin

#define USOIL_POW_PIN 2     // 5TM Power Pin, Upper - White 5TM Wire
#define LSOIL_POW_PIN 38    // 5TM Power Pin, Lower - White 5TM Wire
#define USOIL_SER Serial1   // 5TM Serial Port, Upper RX = D0, TX = D1; Red 5TM Wire
#define LSOIL_SER Serial    // 5TM Serial Port, Lower RX = D31, TX = D30; Red 5TM Wire

#define SONIC_PIN 10        // DS2 Data Pin, Red DS2 Wire

#define ADC_RES 12          // Number of bits Arduino ADC has
#define ADS_LI200_PIN 0     // LiCor Li200 pin on ADS1115
#define ADS_VCC_PIN 1       // VCC pin on ADS1115

#define THERM_PIN A3        // SL-610 Thermistor output
#define THERM_POW 3         // Thermistor power pin
// Positive thermopile pin is in AIN2, negative in AIN3.
// Serial Number: SL-610-SS_1034 !! USES NEW WIRING COLORS !!
// OR
// Serial Number: SL-510-SS_1076 !! USES NEW WIRING COLORS !!






// Libraries --------------------------------------------------------------------------------------
#include <SD.h>			            // SD Card Library
#include <SPI.h>		            // SPI Library
#include "DS2.h"                // DS2 Library
#include "d5TM.h"               // 5TM Library
#include <math.h>               // Math Library - https://www.arduino.cc/en/Math/H
#include <Wire.h>		            // I2C Library
#include <RTClib.h>		          // RTC Library - https://github.com/adafruit/RTClib
#include "DS3231_Alarm1.h"      // RTC Alarm Library Files
#include <Adafruit_SHT31.h>     // SHT31 - https://github.com/adafruit/Adafruit_SHT31
#include <Adafruit_Sensor.h>    // Necessary for BMP280 Code - https://github.com/adafruit/Adafruit_Sensor
#include <Adafruit_BMP280.h>    // BMP280 - https://github.com/adafruit/Adafruit_BMP280_Library
#include <Adafruit_ADS1015.h>   // ADS1115 - https://github.com/soligen2010/Adafruit_ADS1X15
#include <Adafruit_MLX90614.h>  // MLX90614 Library - https://github.com/adafruit/Adafruit-MLX90614-Library



// Initialize Variables----------------------------------------------------------------------------

// Real Time Clock
RTC_DS3231 rtc;                 // Real Time Clock Class
DS3231_Alarm1 rtcAlarm1;        // RTC Alarm
volatile bool rtcFlag = false;  // Used for ISR to know when to take measurements
const uint8_t deltaT = 10;      // Sampling time - Seconds

// SD Card
File logfile;                       // File object
char filename[] = "LEMST_00.CSV";   // Initial filename - Whatever this is named, the filename should be 8 characters long and the last two should be digits!

// ADS1115
Adafruit_ADS1115 ads;
double vcc;                         // Actual value of 3.3V supply voltage

// Battery Level - Max output of 14.6V outputs 3.2444V on A5
double vBat;
const unsigned long R1 = 56000;         // Battery Side Resistor - See https://en.wikipedia.org/wiki/Voltage_divider
const unsigned long R2 = 16000;         // Ground Side Resistor

// MLX90614
#if IR
double mlxIR;                                   // IR values from MLX90614
double mlxAmb;                                  // Ambient temp values from MLX90614
Adafruit_MLX90614 mlx = Adafruit_MLX90614();    // MLX90614 class
#endif

// Upper soil
#if UPPERSOIL
d5TM upperSoil(USOIL_SER, 1200, USOIL_POW_PIN); // Initialize 5TM class
#endif

// Lower soil
#if LOWERSOIL
d5TM lowerSoil(LSOIL_SER, 1200, LSOIL_POW_PIN); // Initialize 5TM class
#endif

// BMP280
#if PRESSURE
Adafruit_BMP280 bmp;         // Initialize BMP280 class
double pressure;             // Barometric pressure
double bmpAmb;               // Temperature from BMP280
double approxAlt;            // Approximate altitude from BMP280
#endif

// Wind
#if WIND
unsigned long startTime;            // Used to measure averaging period for wind speed
volatile unsigned long windCount;   // Counts to convert to speed
double wDir;                         // Wind direction
double wSpd;                         // Wind speed
#endif

#if SUNLIGHT
double rawSun = 0;                       // Float to hold voltage read from ADS1115
const double liConst = 57.80E-6 / 1000;  // Licor Calibration Constant. Units of (Amps/(W/m^2))
const double ampResistor = 59000;        // Exact Resistor Value used by Op-Amp in Ohms
double sunlight = 0.0;                   // Converted Value
#endif

// SHT21
#if TEMPRH
Adafruit_SHT31 sht = Adafruit_SHT31();
double shtAmb;               // Ambient temp values from SHT21
double shtHum;               // Relative humidity values from SHT21
#endif

// DS2
#if SONIC
DS2 sonic(SONIC_PIN, '0');   // Initialize DS2 class
double sonicDir;             // Wind direction from sonic
double sonicSpd;             // Wind speed from sonic
double sonicGst;             // Wind gust from sonic
double sonicTmp;             // Wind temperature from sonic
#endif

// Pyrgeometer
#if PYRGEOMETER

// Thermistor variables
double thermV;            // Voltage reading from arduino ADC for thermistor (volts)
double Rt;                // Thermistor resistance (ohm)
double thermTemp;         // Temperature as measured by thermistor (Kelvin)
double Agz = 9.32793534266128e-4;  // Greater than 0 C thermistor constants
double Bgz = 2.21450736014070e-4;  // "
double Cgz = 1.26232582309837e-7;  // "
double Alz = 9.32959957496852e-4;  // Less than 0 C thermistor constants
double Blz = 2.21423593265217e-4;  // "
double Clz = 1.26328669787011e-7;  // "
unsigned int rawTemp = 0;          // Analog read from thermistor

// Thermopile Constants & variables
double k1 = 9.712;     // Wm^-2 per mV - Serial number 1034
double k2 = 1.028;     // Unitless - Serial number 1034
//double k1 = 9.786;      // Serial number 1076
//double k2 = 1.031;       // "
double pilemV;         // Voltage from thermopile
double LWi;            // Incoming longwave radiation
#endif






// Setup ------------------------------------------------------------------------------------------
// ************************************************************************************************
void setup() {

#if DEBUG
  while (!SerialUSB);
  SerialUSB.begin(9600);
  SerialUSB.println("Starting Sketch");
#endif
  delay(3000);                                  // Allows to unplug before main code starts

  // Set pins
  pinMode(GREEN_LED_PIN, OUTPUT);
  pinMode(RED_LED_PIN, OUTPUT);
  pinMode(CARDSELECT, OUTPUT);
  analogReadResolution(ADC_RES);                // Set arduino resolution to 12 bit - only works on ARM arduino boards

  // Set fan low in case it's plugged in but not wanting to be used
  pinMode(FAN_PIN, OUTPUT);
  digitalWrite(FAN_PIN, LOW);

  // Turn on LED during setup process
  digitalWrite(GREEN_LED_PIN, HIGH);

  // ADS1115 begin
  ads.setGain(GAIN_ONE);        // 1x gain   +/- 4.096V  1 bit = 0.000125V
  ads.begin();

  // Setup registers so interrupts wake board from sleep
  SYSCTRL->VREG.bit.RUNSTDBY = 1;              // Configure regulator to run normally in standby mode, so not limited to 50uA
  SYSCTRL->DFLLCTRL.bit.RUNSTDBY = 1;          // Enable DFLL48MHz clock in standby mode

  // Disable USB device to avoid USB interrupts. Necessitates double press of reset button to upload though
  // This is only needed when DEBUG is 0, AND you want to power the LEMSv2 from USB power for some reason
  //  #if !DEBUG
  //    USBDevice.detach();
  //  #endif

  // RTC Setup
  if (!rtc.begin()) {
    error("Couldn't Find RTC!");
  }

  // Attach Interrupt - Interrupts from RTC used instead of delay()
  attachInterrupt(RTC_ALARM_PIN, rtcISR, FALLING);

  // Check for Card Present
  if (!SD.begin(CARDSELECT)) {
    error("Card Init. Failed!");
  }

  // Check for new filename
  for (uint8_t i = 0; i < 100; i++) {
    filename[6] = '0' + i / 10;
    filename[7] = '0' + i % 10;
    if (! SD.exists(filename)) {
      break;
    }
  }

  // Open file
  logfile = SD.open(filename, FILE_WRITE);
  if (!logfile) {
    error("Couldn't Create File!");
  }
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

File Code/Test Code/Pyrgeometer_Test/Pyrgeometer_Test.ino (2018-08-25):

// Get Apogee SL-610 working

// Libraries 
#include <math.h>
#include <Wire.h>
#include <Adafruit_BMP280.h>    // BMP280 used to get initial temp to calculate thermistor temp
#include <Adafruit_ADS1015.h>

// Defines
#define ADC_RES 12          // Number of bits Arduino ADC has
#define ADS_VCC_PIN 1       // VCC pin on ADS1115
#define THERM_PIN A3        // SL-610 Thermistor output
#define THERM_POW 3         // Thermistor power pin
// Positive thermopile pin is in AIN2, negative in AIN3. Serial Number: SL-610-SS_1034 !! USES NEW WIRING COLORS !!

// BMP280
Adafruit_BMP280 bmp;      // Initialize BMP280 class
double bmpAmb;            // Temperature from BMP280
double approxAlt;         // Approximate altitude from BMP

// Generic variables
Adafruit_ADS1115 ads;     // Use this for the 16-bit version
double vcc;               // VCC 

// Thermistor variables
double thermV;            // Voltage reading from arduino ADC for thermistor (volts)
double Rt;                // Thermistor resistance (ohm)
double thermTemp;         // Temperature as measured by thermistor (Kelvin)
double Agz = 9.32793534266128e-4;  // Greater than 0 C thermistor constants
double Bgz = 2.21450736014070e-4;  // "
double Cgz = 1.26232582309837e-7;  // "
double Alz = 9.32959957496852e-4;  // Less than 0 C thermistor constants
double Blz = 2.21423593265217e-4;  // "
double Clz = 1.26328669787011e-7;  // "
unsigned int rawTemp = 0;          // Analog read from thermistor

// Thermopile Constants & variables
//double k1 = 9.712;     // Wm^-2 per mV - Serial number 1034
//double k2 = 1.028;     // Unitless - Serial number 1034
double k1 = 9.786;      // Serial number 1076
double k2 = 1.031;       // "
double pilemV;         // Voltage from thermopile
double LWi;            // Incoming longwave radiation

  


void setup(void) {
  SerialUSB.begin(9600);
  SerialUSB.println("Starting Test");

  analogReadResolution(ADC_RES);                // Set arduino resolution to 12 bit - only works on ARM arduino boards

  pinMode(THERM_POW, OUTPUT);
  digitalWrite(THERM_POW, LOW);

  bmp.begin();                  // Start BMP280

  ads.setGain(GAIN_SIXTEEN);    // 16x gain  +/- 0.256V  0.0078125mV/bit
  ads.begin();
}




void loop(void) {

  // Read misc variables
  ads.setGain(GAIN_ONE);
  vcc = ads.readADC_SingleEnded_V(ADS_VCC_PIN);       // VCC connected to AIN1
  ads.setGain(GAIN_SIXTEEN);
  bmpAmb = bmp.readTemperature();                     // Temp from BMP280
  approxAlt = bmp.readAltitude(1013.25);              // Technically should be adjusted to local sea level pressure

  // Read thermistor
  digitalWrite(THERM_POW, HIGH);
  rawTemp = analogRead(THERM_PIN);
  digitalWrite(THERM_POW, LOW);
  thermV = double(rawTemp) / (pow(2,ADC_RES)-1) * vcc;
  Rt = 24900.0 * thermV / (vcc - thermV);
  if(bmpAmb >= 0){
    thermTemp = 1.0 / (Agz + Bgz*log(Rt) + Cgz*pow(log(Rt), 3));    // Steinhart-hart Equation
  } else {
    thermTemp = 1.0 / (Alz + Blz*log(Rt) + Clz*pow(log(Rt), 3));   
  }

  // Read thermopile
  pilemV = ads.readADC_Differential_2_3_V()*1000.0;   // Positive thermopile pin is in AIN2, negative in AIN3.
  LWi = k1*pilemV + k2*5.6704e-8*pow(thermTemp, 4);

  // Print
  SerialUSB.print("Approximate Altitude (m): ");
  SerialUSB.println(approxAlt);
  SerialUSB.print("VCC: ");
  SerialUSB.println(vcc);
  SerialUSB.print("Thermistor temperature (C): ");
  SerialUSB.println(thermTemp - 273.15);
  SerialUSB.print("Thermopile voltage (mV): ");
  SerialUSB.println(pilemV, 6);
  SerialUSB.print("Longwave Radiation (Wm^-2): ");
  SerialUSB.println(LWi);
  SerialUSB.println();

  delay(2000);
}

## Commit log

2016-05-03 Added .gitignore
    [Bill of Materials.xlsx]
2016-05-26 Added files, minor changes
    [Bill of Materials.xlsx, Hardware Description.xlsx]
2016-05-27 Added pin connections, other files
    [Adafruit Feather M0 WiFi.brd, Adafruit Feather M0 WiFi.sch, Hardware Description.xlsx]
2016-06-01 Added many sensors to code, datasheets
    [Bill of Materials.xlsx, Hardware Description.xlsx]
2016-06-08 Added transimpedance calculations
    [LEMSv2.sch]
2016-06-10 Added parts to schematic
    [Bill of Materials.xlsx, Hardware Description.xlsx, LEMSv2.sch]
2016-06-21 Added library, more parts to schematic
    [Bill of Materials.xlsx, Hardware Description.xlsx]
2016-06-29 Working test of LEMSv2, soil test
    [Bill of Materials.xlsx]
2016-06-30 Added sensor stick
    [Bill of Materials.xlsx, SensorStick.brd, SensorStick.sch]
2016-07-03 Finished routing sensor stick
    [Bill of Materials.xlsx, SensorStick.brd]
2016-07-17 Commit before converting 5TM to library
    [Adafruit Feather M0 WiFi.brd, Adafruit Feather M0 WiFi.sch, Bill of Materials.xlsx, Hardware Description.xlsx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]
2016-07-21 Added sleep code
    [Bill of Materials.xlsx]
2016-07-25 Changed how parts were added to BOM
    [Bill of Materials.xlsx, LEMSv2.sch, Pin List.xlsx]
2016-07-29 Determined more parts, added to lib/schematic
    [Bill of Materials.xlsx, LEMSv2.sch, Pin List.xlsx]
2016-07-31 Improved BOM and added parts
    [Bill of Materials.xlsx, LEMSv2.sch]
2016-08-02 Added more parts to schematic
    [Bill of Materials.xlsx, LEMSv2.sch, Pin List.xlsx]
2016-08-04 Added circuits to schematic
    [Bill of Materials.xlsx, LEMSv2.sch, Pin List.xlsx]
2016-08-06 Added LED circuit
    [Bill of Materials.xlsx, LEMSv2.sch]
2016-08-06 Added ADC and support parts
    [Bill of Materials.xlsx, LEMSv2.sch]
2016-08-07 Added final schematic parts
    [Bill of Materials.xlsx, LEMSv2.brd, LEMSv2.sch, Pin List.xlsx]
2016-08-08 Modified SD connector footprint, moved connectors
    [LEMSv2.brd, LEMSv2.sch, sparkfun-samd21-pro-breakout-v10.brd]
2016-08-09 Initial layout
    [Bill of Materials.xlsx, LEMSv2.brd, LEMSv2.sch]
2016-08-11 5TM library bug fix, board layout changes
    [Bill of Materials.xlsx, LEMSv2.brd, LEMSv2.sch]
2016-08-12 Fixed other 5TM checksum bug
    [Bill of Materials.xlsx]
2016-08-14 Switched 5TM power to transistor, added schottky
    [Bill of Materials.xlsx, LEMSv2.brd, LEMSv2.sch]
2016-08-15 Started routing, part changes
    [Bill of Materials.xlsx, LEMSv2.brd, LEMSv2.sch, Pin List.xlsx]
2016-08-16 More routing
    [Bill of Materials.xlsx, LEMSv2.brd, LEMSv2.sch, Pin List.xlsx]
2016-08-18 File reorganization
    [Bill of Materials.xlsx, SensorStick.brd, SensorStick.sch, sparkfun-samd21-pro-breakout-v10.brd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]
2016-08-18 Completed board
    [Bill of Materials.xlsx, LEMSv2.brd, LEMSv2.sch]
2016-08-24 Added gerbers and centroid files
    [Bill of Materials.xlsx, LEMSv2 Centroid SC.csv, LEMSv2.brd, LEMSv2.drills.xln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]
2016-08-25 Soldermask changes and started assembly quotes
    [Bill of Materials.xlsx, LEMSv2.brd]
2016-08-31 Added assembly quotes and panelized gerbers
    [Bill of Materials.xlsx, LEMSv2.merged.drills.xln]
2016-09-09 Updated BOM, design finalized for assembly
    [Bill of Materials.xlsx, LEMSv2.merged.drills.xln]
2016-09-29 File reorganization, README update, Time_Set added
    [Bill of Materials.xlsx, LEMSv2 Centroid SC.csv, LEMSv2.brd, LEMSv2.drills.xln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]
2016-10-02 Added Li200 Base
    [Base.SLDASM, Base.STL, Bill of Materials.xlsx, Holder.SLDPRT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]
2016-10-06 Updated base without post
    [Base.SLDASM, Base.STL, Holder.SLDPRT, Sphere.SLDPRT]
2016-10-20 Added calibration constants workbook
    [Bill of Materials.xlsx, Calibration Constants.xlsx]
2016-10-24 Added modified old Li200R Base
    [2147A610 Plastic Level.SLDPRT, 90866A111 Wingnut.SLDPRT, 92311A544 Set Screw.SLDPRT, 95475A509 Rod.SLDPRT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]
2016-11-07 Small BOM and documentation changes
    [Bill of Materials.xlsx, Wiring Information.xlsx]
2016-11-13 Added more instructions
    [Bill of Materials.xlsx, Wiring Information.xlsx]
2016-11-14 Added possible problem
    [Wiring Information.xlsx]
2016-11-29 BOM update
    [Bill of Materials.xlsx]
2016-12-17 Minor changes and added simple matlab data viewing script
    [Bill of Materials.xlsx]
2017-05-16 Added DS2 sonic code
    [Bill of Materials.xlsx]
2017-05-18 Fixed sonic header printing bug
2017-06-02 Updated MLX housing instructions
    [Bill of Materials.xlsx]
2017-06-12 Minor README changes
    [Bill of Materials.xlsx]
2017-09-29 Added LEMS scaling to BOM
    [Bill of Materials.xlsx]
2018-03-11 Updates and preparation for 2018 builds/deployments
    [Bill of Materials.xlsx, Wiring Information.xlsx]
2018-07-01 Atmos 22 code now working
    [Bill of Materials PCB.xlsx, Bill of Materials.xlsx, Pin List.xlsx, Wiring Information.xlsx]

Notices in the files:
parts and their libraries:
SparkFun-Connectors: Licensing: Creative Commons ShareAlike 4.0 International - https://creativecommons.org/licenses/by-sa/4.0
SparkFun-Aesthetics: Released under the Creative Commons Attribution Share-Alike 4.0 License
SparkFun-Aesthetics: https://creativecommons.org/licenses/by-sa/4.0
